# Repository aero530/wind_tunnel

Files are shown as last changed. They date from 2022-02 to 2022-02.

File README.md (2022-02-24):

# wind_tunnel

Low speed wind tunnel made from scrap material and 12V DC computer fans capable of 0 to 1200 ft/min.

Calibration process is documented [here](pitot%20static%20tube%20calibration%20process/Thermal%20Load%20Card%20Pitot%20Static%20Tube%20Calibration.pdf)

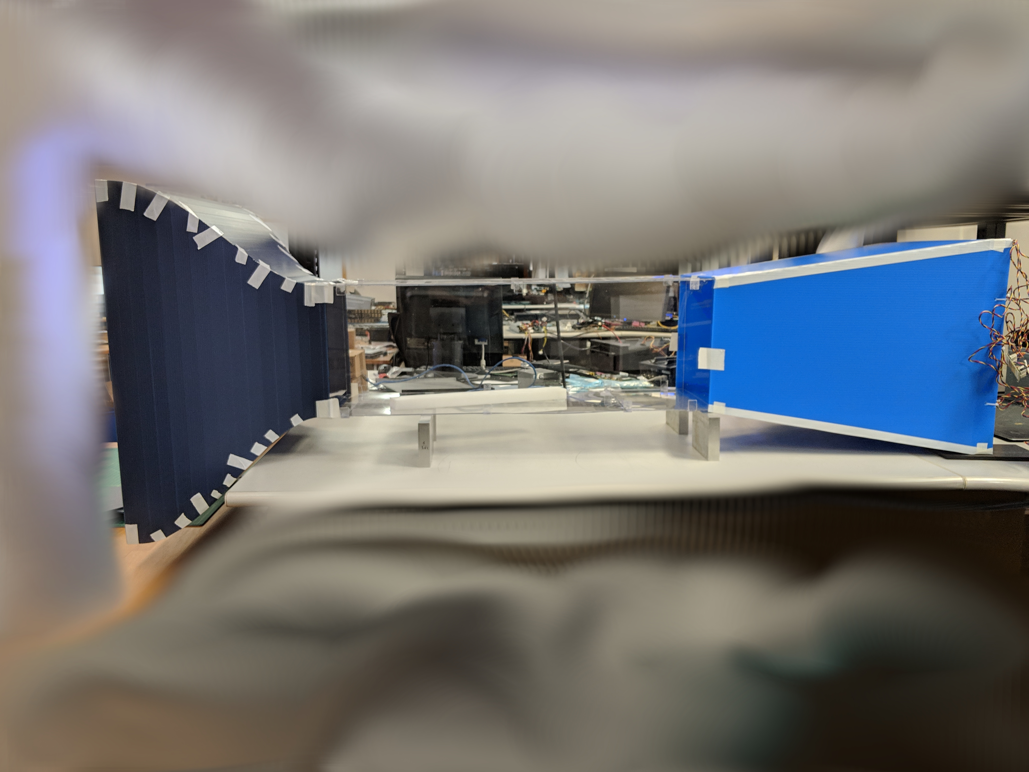
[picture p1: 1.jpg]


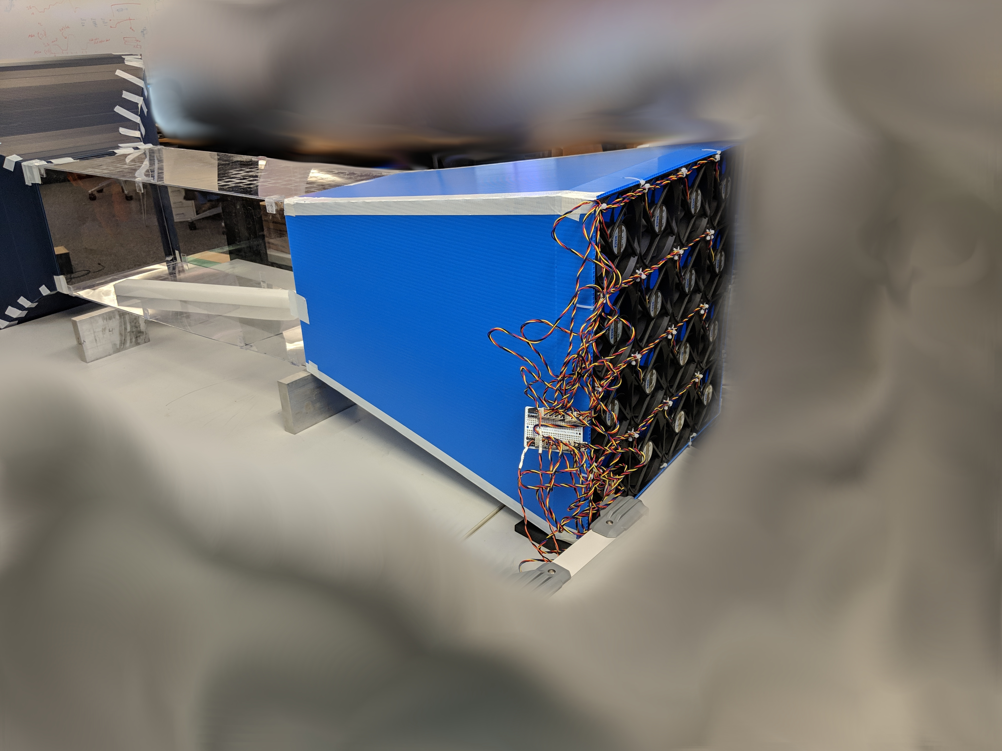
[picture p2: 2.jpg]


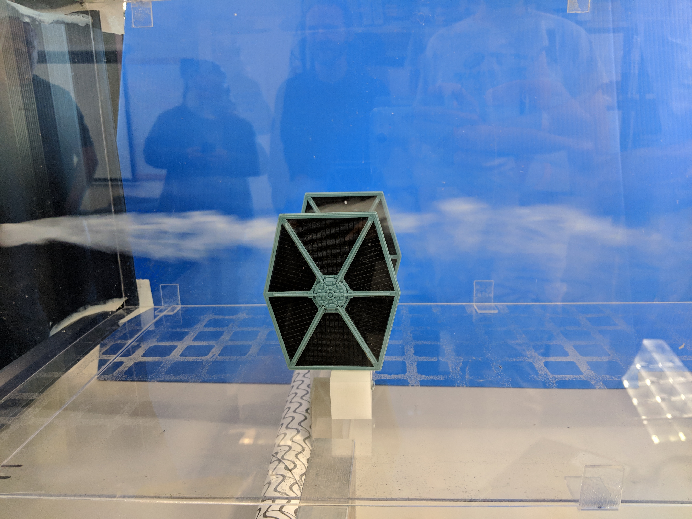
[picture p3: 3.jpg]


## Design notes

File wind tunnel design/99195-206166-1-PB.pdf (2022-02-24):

Indian Journal of Science and Technology, Vol 9(30), DOI: 10.17485/ijst/2016/v9i30/99195, August 2016

ISSN (Print) : 0974-6846
ISSN (Online) : 0974-5645

* Author for correspondence

## 1. Introduction

The wind tunnel is a tool to study fluid flows around a body and the forces generated by the fluid-structure interaction. Using such tool, it is possible to measure global and local flow velocities, as well as pressure and temperature around the body. A wind tunnel experiment provides the force and pressure values on the model and the flow visualization. It is a critical instrument in the quick and thorough design process of anything that involves fluid dynamics. Based on the flow through the tunnel circuit, the wind tunnel is of two types, open type and closed type. In open type, ambient air enters from one side and exits to the atmosphere after flowing through the tunnel. In closed type wind tunnel, a constant volume of air is allowed to pass through the tunnel circuit continuously Figure 1.

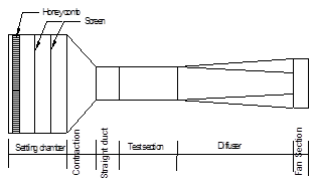
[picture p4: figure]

Figure 1. Schematic diagram showing different parts of wind tunnel.

Abstract

Objectives: This paper elucidate the entire procedure to design an open circuit subsonic wind tunnel which will be used to study the wind effect on the different prototypes of structural elements. Method: The existing guidelines and findings of the previous research works were followed for design calculation of different parts of the wind tunnel. Three design trials have been performed so as to achieve a velocity of 25 m/s at the test section. The final trial has been discussed in the body of the paper. Findings: The design includes a square test section of side 500 mm, to accommodate the model and required instrumentation in it, for force and pressure measurement. A straight section before the test chamber is provided to allow the output of contraction section to stabilize before it reaches the test section. Instead of using a curved wall shape a straight contraction profile with larger contraction length is used. The diffuser extends from the test section and its cross section changes from a square test section to an octagon of 311 mm side. The pressure drop and power required for the designed wind tunnel are calculated and tunnel performance curve is plotted. Application: The design being purely empirical, it requires computational validation before commencement of the construction of the wind tunnel. The investigators have actually made an attempt to design the same in the existing setup, which may be useful for different research purpose.
Keywords: Design of Open Circuit Wind Tunnel, Loss in Contraction Section, Power Requirement, Pressure Drop in

# Diffuser, Stilting Section, Tunnel Performance Curve

# Design of Low Cost Open Circuit Wind Tunnel – A Case Study

Mahesh K. Panda*

and Amiya K. Samanta
Department of Civil Engineering, National Institute of Technology Durgapur - 713209, West Bengal, India; mahesh26119@gmail.com, aksnitd@gmail.com

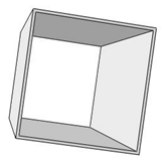
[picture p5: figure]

2 | Vol 9 (30) | August 2016 | www.indjst.org | Indian Journal of Science and Technology

Design of Low Cost Open Circuit Wind Tunnel – A Case Study

The main goal of wind tunnel design is to have uniform flow within the test chamber. Test chamber dimension depends on the type of test to be performed and the size of the model to be tested. The wind tunnel’s overall dimensions are key factors in its construction and running costs. The trade-off is required between the opposing needs to get a suitable design of the wind tunnel, satisfying the test requirements, space and budget constraints¹

. The design process starts by defining the test chamber dimensions and shape, after that the rest part of the wind tunnel is designed by keeping in view the dimensions of the test chamber.
Principal parts of an open type wind tunnel are the test section, contraction, diffuser, settling chamber and driving unit (Fan). This paper deals with the design of an open type wind tunnel to have minimum construction cost and the running cost.

## 2. Design Methodology

The open circuit wind tunnel is made of several distinct sections, the settling chamber, the contraction cone, the test section, the diffuser and the fan. Different parts are described as follows:

### 2.1 Test Section

The wind tunnel design starts with deciding the test section keeping an eye on the accessibility and installation of the test model and instrumentation. From the experimental investigations, it has been found that the blockage has an almost negligible effect on test results when it is about 10%²

. The test chamber length has to be in the range of 0.5-3 times its hydraulic diameter³,4. The test chamber is being designed to test the scaled model of a silo with length 250 mm and minimum L/D ratio 1. In order to have a blockage ratio less than 10% a square test chamber of 500 mm side is chosen Figure 2. The test will be carried out at a flow speed of 25 m/s. The pressure loss coefficient goes on increasing with increase in the test section Figure 3. So the length of test section should be as small as possible. The length of the test chamber was set to 1.25 m i.e. 2.215 times the hydraulic diameter of the test section.

Figure 2. Test section.

### 2.2 Contraction Cone

The contraction accelerates the flow to the test section, further reducing any variations in velocity. A contraction design satisfying all criteria will be such that the separation is just avoided and the exit non-uniformity is equal to or less than the maximum tolerable level for the desired application in shortest possible length⁵

. The contraction
starts with the selection of contraction ratio⁶

. For smaller
tunnels the contraction ratio should be in between 6 to 9. The length of the contraction should be in between 0.15 R to R. R being the hydraulic radius of the contraction section inlet. Too large contraction section avoids flow separation⁷
As shown in Figure 4, the pressure drop coefficient values go on decreasing with increase in CR, so the maximum allowable contraction ratio 9 is chosen. To avoid flow separation, a contraction of length of 900 mm is used, which is 20% longer than the maximum recommended value. For easier and cheaper construction a straight contraction shape is used instead of solving complex equations to get the wall shape. The nozzle exit cross section dimensions and shape are identical to the test chamber.
250 | 500 | 750 | 1000 | 1250 | 1500 | 1750

0.01

0.02

0.03

0.04

0.05

0.06

Pressure drop coefficent

Length of test section (mm)

Figure 3. Plot to show the pressure loss in a constant area section.

Mahesh K. Panda and Amiya K. Samanta

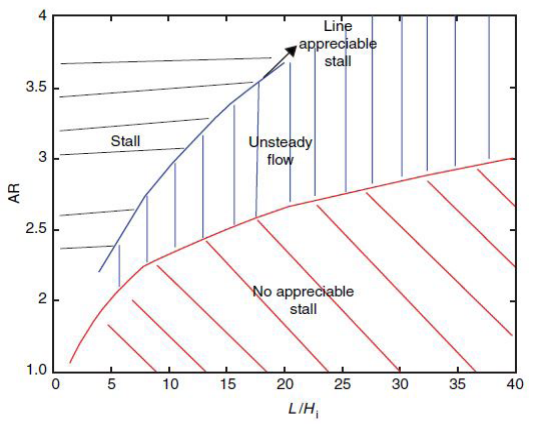
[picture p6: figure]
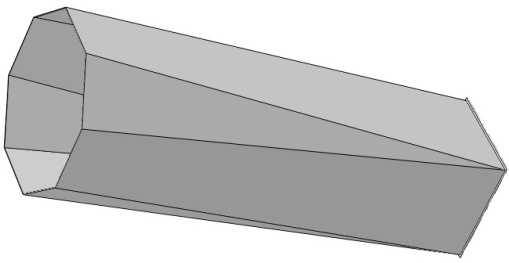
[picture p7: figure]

Vol 9 (30) | August 2016 | www.indjst.org | Indian Journal of Science and Technology | 3

5.5 6.0 6.5 7.0 7.5 8.0 8.5 9.0 9.5 10.0 10.5 11.0 0.0030

0.0032

0.0034

0.0036

0.0038

0.0040

0.0042

0.0044

0.0046

0.0048
Loss coefficient

Contraction Ratio

Loss coefficient

Figure 4. Contraction section pressure loss coefficient with contraction ratio.

### 2.3 Straight Section

Inserting a small settling duct before the test section can reduce the turbulence level to an acceptable level, for nonstreamlined shape of contraction wall⁸

. A straight section
of length 0.5 m has been inserted after the contraction, with an area of cross section equal to the testing chamber size. Figure 5 shows the straight section attached to the contraction cone.

Figure 5. A diagram showing the contraction cone with a straight section.

### 2.4 Diffuser

The diffuser is mainly used to reduce the velocity of flow in the shortest possible distance to reduce the load on drive system. The flow through the diffuser depends on its geometry defined by area ratio (ratio of outlet area to the inlet area) and diffuser angle (2θ), wall contour and diffuser cross-sectional shapes. The area ratio of the diffuser should be less than 2.5 and diffuser angle should be 5˚ – 7˚ for controlling flow separation. The minimum length of diffuser can be found from Equation,
. | (1)

Where, Dh1 is the inlet sections hydraulic diameter and is the half of the included angle of the diffuser cone.
| Assuming minimum diffusion angle (θe ) i.e. 5⁰ and
solving for L, the maximum of the minimum length of the diffuser is found to be 2.38 m, hence a diffuser of 2.5 m length is provided. An octagonal outlet is chosen with side 310 mm Figure 6. The diffuser area ratio is calculated as 1.86, which falls in the no stall region in Figure 7 with a diffusion angle 5.03⁰

Figure 6. A diagram showing the diffuser.

### 2.5 Settling Chamber

The aim of a settling chamber containing honeycombs and screens is to reduce the flow turbulence before it enters the cone. A selection of honeycomb and screens for a wind tunnel is very much dependent on the test type to which the tunnel is intended⁸

. The settling
chamber cross-sectional area matches the dimensions of contraction cone inlet i.e. 1.5 m x 1.5 m with a length equal to 1.25 m is used.

### 2.6 Honeycomb

The honeycomb removes the swirl from the incoming flow and minimizes the variation in both mean and fluctuating velocity⁹

. It should have sufficient flexural rigidity to withstand applied forces during operation without significant deformation. The primary design parameter for honeycomb is the ratio of length to cell hydraulic diameter (L/D) and porosity (flow area upon total area). Recommended L/D ratio for honeycomb is 6 to 8 with porosity nearly 0.8. A square shaped honeycomb, 3 mm

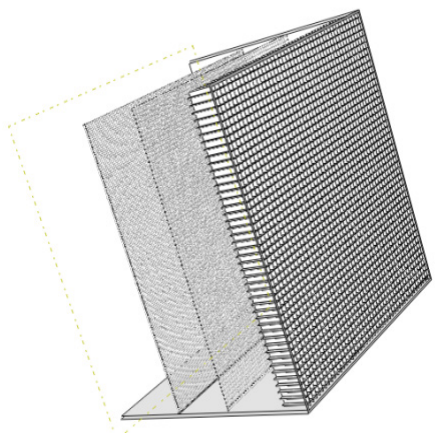
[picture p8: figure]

4 | Vol 9 (30) | August 2016 | www.indjst.org | Indian Journal of Science and Technology

thick and 27 mm size and 150 mm length is provided with a porosity value of 0.82. Figure 8 shows an arrangement of Honeycomb and screens in settling chamber.

Figure 8. Diagram showing the arrangement of honeycomb and screen.

### 2.7 Screens

Tensioned screens are placed in the settling chamber for the reduction of turbulence level of incoming flow, this breaks up the large scale turbulent eddies into a number of small scale eddies that subsequently decay. To be effective in reducing turbulence a screen must have porosity in the range 0.58–0.8⁹

. Screen porosity values over 0.8 are not suitable for good turbulence control while values below 0.58 lead to flow instability¹⁰. A clearance of 0.2 times the settling chamber diameter is required between the screens. Experimentally it is found that better turbulence control can be achieved when the finest screen is placed farthest downstream¹¹⁻¹³.
So a screen with 2 mm wire and porosity 0.69 is placed at a distance 340 mm from the start of the contraction i.e. 0.2 times the hydraulic diameter of the settling chamber and the 3 mm wire screen mesh with porosity 0.76 is placed at the same distance from the first screen.

### 2.8 Drive System

The drive system compensates the loss in the circuit and determines the movement of the fluid through the test section. For an air tunnel, two primary drive systems are a compressor and fan. In our case, an Axial fan will be used as these are high efficient and produce air flow with less turbulence. After the maximum required fan static pressure and volume flow rate have been estimated the maker’s performance chart can be consulted to choose a fan with optimum efficiency, RPM and required power¹⁴.

## 3. Losses in Wind Tunnel Circuit

For loss calculation, the tunnel can be divided into sections. The pressure loss in a tunnel section is defined as the mean loss of total pressure sustained by the stream, in passing through the particular section. The energy loss of each section can be written in dimensionless form as
pressure drop coefficient | | (2)

Where, is test section dynamic pressure given as
| | (3)

The losses in different parts of wind tunnel can be calculated as below:

### 3.1 Pressure Losses in Constant Area Sections

Considering a constant-area section (A), the pressure loss (p) along the duct is proportional to its length (L), hydraulic diameter (Dh

), fluid density (ρ) and constant of proportionality is the friction factor (f). The loss
coefficient is given by, | . | (4)
The friction loss coefficient can be determined by using universal law of friction to determine the friction factor in 4 to 6 iterations with an initial value of 1. In Equation is given as:
| | (5)

### 3.2 Pressure Loss in Diffuser

Pressure loss in the diffuser is due to the skin friction loss and the expansion loss. The main parameters are equivalent conical expansion angle ( ) and the ratio between inlet and outlet cross section areas (Ar

| | ). The
loss coefficient is the sum of the two loss factors, the first relates to friction and the second to expansion
| | (6)
For one dimensional flow, the frictional loss coefficient is
given as | | (7)

and the expansion loss is calculated by the empirical
relationship | | (8)
The term | can be expressed as a geometrical
function depending upon the expansion angle and the cross section shape of the diffuser. In our case > 5⁰

,
so = A3+B3 , | | (9)
for circular section the values of A3 and B3 are -0.0966

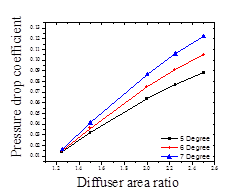
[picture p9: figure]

Vol 9 (30) | August 2016 | www.indjst.org | Indian Journal of Science and Technology | 5

and 0.04672 respectively. For square section the values of A3 and B3 are -0.0132 and 0.05866 respectively. Figure 9 shows the variation of pressure loss coefficient with area ratio for different diffusion angle.

Figure 9. Plot showing the pressure drop for various diffusion angle.

### 3.2 Contraction Section Loss

The pressure loss in contraction is due to skin friction. The loss coefficient in the contraction is given by¹⁵:

(10)
Where, L0

is the length of contraction, D0

the test
section diameter, Di

the inlet cone diameter, and f is friction coefficient.

### 3.2 Stilting Section Loss

The losses in the settling chamber are primarily due to the honeycomb and screens used for turbulence reduction. The loss in the honeycomb can be calculated from the formula
(11)

Where
(12)

The screen loss coefficient can be calculated

(13)

Is screen solidity and is the screen porosity. is the mesh factor equal to 1.0 for new metal wire , 1.3 for average circular metal wire, and 2.1 fir silk thread and kRn is given as

(14)
From the Equations it is clear that the pressure drop through the honeycomb and the screen depends only upon the characteristics of the same and becomes constant when the Reynolds number values exceed some critical value. Honeycomb loss depends on L/D ratio of honeycomb and porosity while the pressure drop through the screen is dependent on the type of wire and the porosity.

## 4. Power required in Wind Tunnel

Power required for maintaining a steady flow through the wind tunnel is equal to the total losses occurring in the flow through the tunnel. These losses are due to kinetic energy being dissipated by vortices and turbulence. The loss in kinetic energy, which appears as a decrease in total pressure must be compensated by a pressure rise, usually provided by a fan. Thus if the power input to the fan is P (i.e. the motor shaft output) and the fan has an efficiency the equation balancing the energy input to the stream to the energy losses in the tunnel is
(15)
The required power for a given section size and flow conditions depends on the sum of the pressure drop coefficient (ki

) in the individual tunnel sections. The pressure loss equation for subsonic flow in wind tunnel is
given as | | (16)
In the designed tunnel the various loss coefficient are given in Table 1, for a speed of 25m/s at the test section. Speed at fan section: = (25*0.5*0.5)/ (0.25*3.142*.75*.75)
| = 14.144 m/s
The pressure loss in the tunnel circuit is equal to:
= ( | ) ∑ ki + loss at fan section | (17)
= 0.5*1.225*25² *1.3553+ 0.5*1.225*14.144*14.144 =641.36 Pa

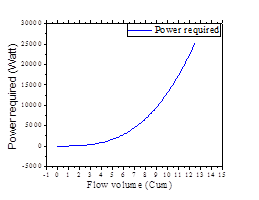
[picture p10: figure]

6 | Vol 9 (30) | August 2016 | www.indjst.org | Indian Journal of Science and Technology

Table 1. Tunnel pressure loss coefficient at test section velocity 25 m/s
Wind Tunnel Section | Loss coefficient
Honeycomb | 0.2200
Screen 1 | 0.4117
Screen 2 | 0.6049
Contraction | 0.0037
Straight section | 0.149
Test Section | 0.372
Diffuser | 0.0629
Total | 1.3553

The power required by the tunnel is equal to:
= Q * ∆Pa = (A*V)* ∆Pa | (18)
= (0.25*3.142*0.75²

*14.144)*641.36 = 4008.5 Watt

The power required for given flow in the wind tunnel test section is calculated and the same is plotted as the tunnel performance curve. Figure 10 shows the tunnel performance curve for the designed wind tunnel. Fan performance curves, which are supplied by the fan manufactures, can be plotted on the tunnel performance curve and the fan with maximum efficiency that intersects the tunnel performance curve is to be chosen for use in the tunnel.

Figure 10. Tunnel performance.

## 5. Conclusion

The fan/motor to be fitted in the tunnel should be chosen conservatively to have desired flow velocity in the wind tunnel test section to cater the unseen losses in the tunnel. Further due to the purely empirical design of wind tunnel, as per the guidelines of the previous researchers, the design is required to be verified computationally as well as experimentally. First the tunnel design is to be tested for the desired flow quality and pressure loss in the tunnel computationally through any high-end simulation software (ABAQUS or ANSYS) if satisfactory results are found then the wind tunnel can be built. Before carrying out any experiment, the wind tunnel performance is to be tested and calibrated.
To ensure good performance of the structures subjected to wind loads, their behavior must be anticipated in advance by the design engineer¹⁶. Model studies through wind tunnel facilitate the same for the intended structure. So it is a useful tool in wind engineering.

## 6. References

1. Cattafesta L, Bahr CJ, Mathew J. Fundamentals of wind‐ tunnel design. Encyclopedia of Aerospace Engineering; 2010 Dec. p. 1–10.
2. Roy S, Saha UK. An adopted blockage factor correlation approach in wind tunnel experiments of a Savonius-style wind turbine. Energy Conversion and Management. 2014; 86(6):418–27.
3. Arifuzzaman, MM. Design construction and performance test of a low cost subsonic wind tunnel. IOSR Journal of Engineering. 2012 Oct; 2(10):83–92.
4. Barlow JB, Rae WH, Pope A. Low-speed wind tunnel testing. 3rd Ed. Wind Tunnel Design. United States of America: John Willey and Sons Publ; 1999.
5. Abdalhamed AS, Yassen YEl-S, Elssaka MM. Design optimization of three dimensional geometry of wind tunnel contraction. Ain Shams Engineering Journal. 2015 Mar; 6(1):281–8.
6. Fang FM, Chen JC, Hong YT. Experimental and analytical evaluation of flow in a square to square wind tunnel contraction. Journal of Wind Engineering and Industrial Aerodynamics. 2011 Mar; 89(3-4):247–62.
7. Mehta RD, Bradshaw P. Design rules for small low speed wind tunnels. The Aeronautical Journal. 1979 Nov; 83(827):443–9.
8. Building a wind tunnel: It will blow your mind. 2008. Available from: http://www.tomcarlone.com/Wind TunnelProject/WindTunnelReport.pdf
9. Gharbanian K, Soltani MR, Manshadi D. Experimental investigation on turbulence reduction in subsonic wind tunnels. Aerospace Science and Technology. 2011 Mar; 15(2):137–47.

Vol 9 (30) | August 2016 | www.indjst.org | Indian Journal of Science and Technology | 7
10. Mehta RD. Turbulent boundary layer perturbed by a screen. AIAA Journal. 1985 Sep; 23(9):1335–42.
11. Quiterio PR, Velazquez MT, Eslava GT, Eslava RT, Florencio SS, Francis JA. Wind tunnel at LABINTHAP (Updated). Energy and Power Engineering. 2011 Sep; 3(4):565–73.
12. Groth J, Johansson AV. Turbulence reduction by screen. Journal of Fluid Mechanics. 1988 May; 197:139–55.
13. Gharbanian K, Soltani MR, Manshadi MD. Experimental investigation on turbulence reduction in subsonic wind tunnels. Aerospace Science and Technology. 2011 Mar; 15(2):137–47.
14. Bleier FP. Fan handbook: Selection application and design. New York: McGraw Hills Publications; 1998.
15. D Space. 2016. Available from: https://en.wikipedia.org/wiki/DSpace
16. Kumar BD, Swami BLP. Wind effects on tall building frames-influence of dynamic parameters. Indian Journal of Science and Technology. 2010 May; 3(5):583–7.

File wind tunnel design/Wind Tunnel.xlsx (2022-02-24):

Test item cross section area | 8 | in^2
Test height | 12 | in | assume square test section
Test area ratio | 18 |  | should be >10
Test Hydraulic Diameter | 12 | in
Test Length Ratio | 2 |  | should be 0.5 to 3 times Dh
Test Length | 24 | in
Contraction Ratio | 5.84 |  | should be 4 to 9
Contraction Angle | 31.26 | deg
Inlet height | 29.00 | in
Contraction Length | 14.00 | in
Contraction Length Ratio | 0.483 |  | should be 0.15 to 1
Desired LFM | 1500 | ft/min
CFM | 1500 | CFM
Diffuser Angle | 7.94 | deg | should be 5-8deg
Diffuser Area Ratio | 2.5 |  | should be less than 2.5
Exit height | 18.974 | in
Exit height | 481.931 | mm
Diffuser Length | 25.000 | in
Per Fan Airflow | 100 | CFM
# Fans that fit | 16
# Fans needed | 15
Total Length | 63.002 | in
Total Length | 5.25 | ft

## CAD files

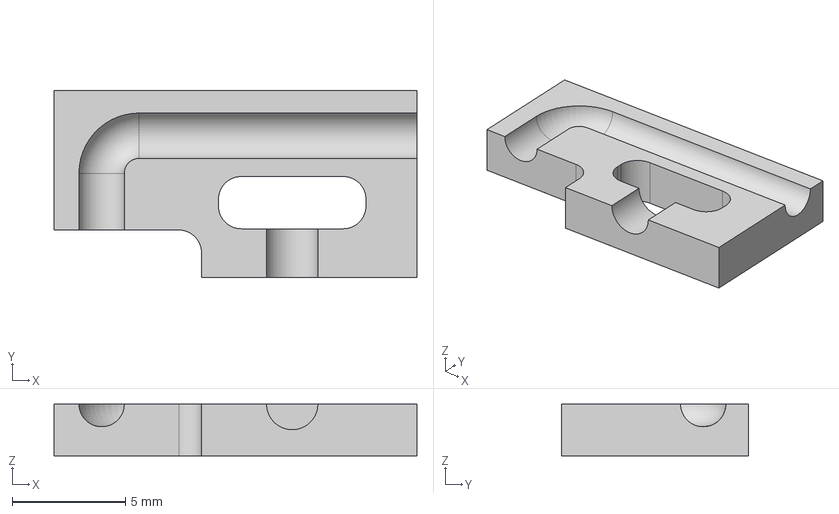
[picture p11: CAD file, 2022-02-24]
pitot static tube design/cad/SDP3X pitot tube 1 v1.step
16.0 x 8.26 x 2.29 mm

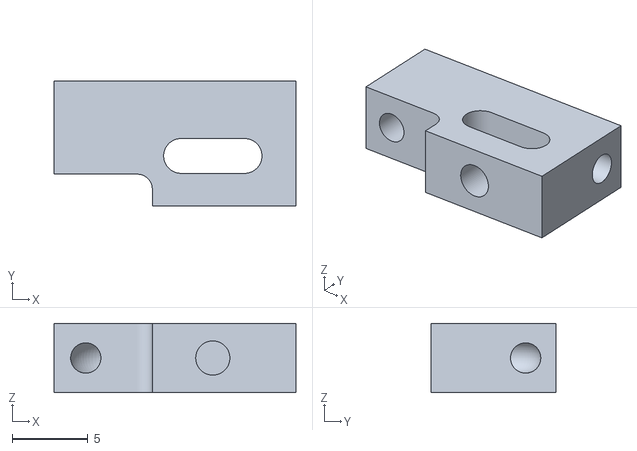
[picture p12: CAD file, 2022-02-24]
pitot static tube design/SDP3X pitot tube solid.STL
16.0 x 8.26 x 4.57

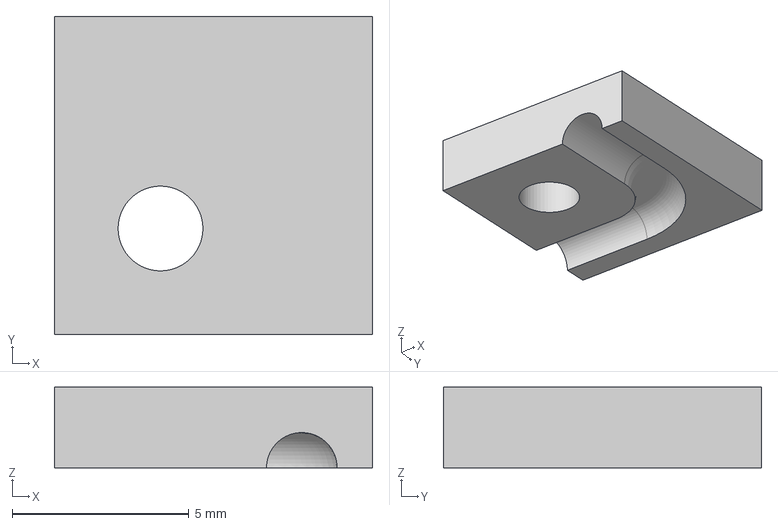
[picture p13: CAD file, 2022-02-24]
pitot static tube design/cad/Amphenol DLHR-L01D-E1BD Pitot Tube B v1.step
9.00 x 9.00 x 2.29 mm

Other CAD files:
pitot static tube design/cad/SDP3X pitot tube 2 v1.step
pitot static tube design/cad/Amphenol DLHR-L01D-E1BD Pitot Tube A v1.step
pitot static tube design/cad/Amphenol DLHR-L01D-E1BD Pitot Tube A v1.iges
pitot static tube design/cad/Amphenol DLHR-L01D-E1BD Pitot Tube A v1.stl
pitot static tube design/cad/Amphenol DLHR-L01D-E1BD Pitot Tube B v1.iges
pitot static tube design/cad/Amphenol DLHR-L01D-E1BD Pitot Tube B v1.stl
pitot static tube design/cad/SDP3X pitot tube 1 v1.iges
pitot static tube design/cad/SDP3X pitot tube 1 v1.stl
pitot static tube design/cad/SDP3X pitot tube 2 v1.iges
pitot static tube design/cad/SDP3X pitot tube 2 v1.stl

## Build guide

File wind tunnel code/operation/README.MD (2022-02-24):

# Wind Tunnel

This code runs a profile on the wind tunnel and collects data from the thermal load card and the hot wire anemometer.  It is super hacky and disgusting code that controls the actual wind tunnel using a python script and collects data from the hot wire anemometer and thermal load card using javascript.

## To run, please:
1. Install python3
2. Install python modules
	`pip install pyserial`
3. Install node/npm
4. Install the required packages by navigating to the containing directory and running `npm install`
5. Configure the settings for COM and test parameters in runTest.py and windTunnel.js
6. From the containing directory, execute `node windTunnel`

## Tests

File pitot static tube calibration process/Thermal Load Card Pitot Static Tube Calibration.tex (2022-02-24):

\documentclass[]{article}
\usepackage{array}
\usepackage{graphicx} % Required for including pictures
\usepackage{float} % float package used so figure location can be forced

\usepackage[top=1in,bottom=1in,left=1in,right=1in,headsep=10pt,letterpaper]{geometry} % Page margins

%----------------------------------------------------------------------------------------
%	FONTS
%----------------------------------------------------------------------------------------

\usepackage{avant} % Use the Avantgarde font for headings
%\usepackage{times} % Use the Times font for headings
\usepackage{mathptmx} % Use the Adobe Times Roman as the default text font together with math symbols from the Sym­bol, Chancery and Com­puter Modern fonts

\usepackage{microtype} % Slightly tweak font spacing for aesthetics
\usepackage[utf8]{inputenc} % Required for including letters with accents
\usepackage[T1]{fontenc} % Use 8-bit encoding that has 256 glyphs

\newenvironment{conditions}
{\par\vspace{\abovedisplayskip}\noindent\begin{tabular}{>{$}l<{$} @{${}={}$} l}}
	{\end{tabular}\par\vspace{\belowdisplayskip}}

%opening
\title{Thermal Load Card Pitot Static Tube Calibration}
\author{Phil Spindler}

\begin{document}

\maketitle

\begin{abstract}

The following summarizes the process for calibrating the thermal load card pitot static tube velocity measurements.  During this process a wind tunnel was used to provide a uniform stream of air with controllable velocity and a hot wire anemometer was used to provide the reference velocity measurements.  The resulting calibration allows for the pitot static tube to produce results within $5\%$ of the hot wire anemometer readings for velocities above $30 \frac{ft}{min}$.

\end{abstract}

\section{Physics Based Calculation}

The primary calculation to convert the differential pressure measured across the ports of the pitot static tube is shown in Equation \ref{basePhysics}.

\begin{equation}\label{basePhysics}
V = \frac{P_0}{P}\sqrt{\frac{T}{T_0}}\sqrt{2 \frac{\partial P_{sensor}}{\rho_0}}
\end{equation}
where:
\begin{conditions}
 V		& velocity in $\frac{m}{s}$ \\
 P_0	& sensor reference pressure $\left[ 966 \mbox{ mbar} \right] $ \\
 P		& atmospheric pressure $\left[1013.25 \mbox{ mbar} \right] $ \\
 T_0	& sensor reference temperature $\left[298.15 \mbox{ K} \right] $ \\
 T		& sensor measured temperature in K \\
 \partial P_{sensor}	& sensor zero calibrated differential pressure in Pa \\
 \rho_0	& density of air $ \left[ 1.1289 \frac{kg}{m^3} \right] $ \\
\end{conditions}

\noindent
Simplifying Equation \ref{basePhysics} gives

\begin{equation}\label{simplifiedPhysics}
V = 0.073490358 \sqrt{ T * \partial P_{sensor} }
\end{equation}

\noindent
Equation \ref{simplifiedPhysics} can be converted from $\frac{m}{s}$ to $\frac{ft}{min}$ by multiplying by $196.85$ leading to Equation \ref{simplifiedPhysicsFt}.

\begin{equation}\label{simplifiedPhysicsFt}
V = 14.4665769723 \sqrt{ T * \partial P_{sensor} }
\end{equation}

\noindent
Equation \ref{simplifiedPhysicsFt} provides the basis to convert the temperature and differential pressure readings from the pitot static tube sensor to velocity.  The calculated velocity values were then put through a calibration process to better match readings from the hot wire anemometer.

\section{Calibration}

The calibration was performed by taking measurements from the pitot static tube on the card and a hot wire anemometer next to the card (approximately 1in away).  The thermal load card was setup in a wind tunnel and the wind tunnel speed was varied through it's entire range (0-100\%) in 1\% increments.  The wind tunnel was held at a constant speed for 30 seconds between each step as shown in Figure \ref{fig:tunnelSetting}.

\begin{figure}[H]
	\centering
	\caption{Wind Tunnel Setting}
	\label{fig:tunnelSetting}
\end{figure}

\noindent
The velocity in the wind tunnel as recored by the hot wire anemometer and results from the pitot static tube based on Equation \ref{simplifiedPhysicsFt} are shown in Figure \ref{fig:rawVelocity}.  The results shown here (and used in subsequent analysis) are an average of 10 seconds of data centered on the middle of the wind tunnel speed steps shown in Figure \ref{fig:tunnelSetting}.  The 10 second subset of data was selected to avoid velocity instabilities in the wind tunnel immediately after wind tunnel setting changes.

\begin{figure}[H]
	\centering
	\caption{Uncalibrated Velocity}
	\label{fig:rawVelocity}
\end{figure}

\noindent
Figure \ref{fig:calibration} shows the physics based calculation of velocity relative to readings from the hot wire anemometer.  This relation was used to create a two part curve fit to calibrate the pitot static tube results with the hot wire anemometer results.  The correlation is linear for velocities above $362.645 \frac{ft}{min}$.  Below that point, the pitot static tube response is non-linear and fit with a second order polynomial.  

\begin{figure}[H]
	\centering
	\caption{Pitot Tube Calibration Curves}
	\label{fig:calibration}
\end{figure}

\noindent
Figure \ref{fig:result} shows the calibrated velocity results.  In this image, the $1:1$ Line shows an ideal fit between the two parameters.  When the airflow velocity is less than approximately $30 \frac{ft}{min}$ the pitot static tube provides unreliable results (with errors up to $93\%$).  Beyond this lower threshold the average error is $1.02\%$ and the maximum error is $4.59\%$.

\begin{figure}[H]
	\centering
	\caption{Calibration Result}
	\label{fig:result}
\end{figure}

\end{document}

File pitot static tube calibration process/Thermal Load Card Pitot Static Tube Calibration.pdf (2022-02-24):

# Thermal Load Card Pitot Static Tube Calibration

Phil Spindler

May 1, 2019

Abstract

The following summarizes the process for calibrating the thermal load card pitot static tube velocity measurements. During this process a wind tunnel was used to provide a uniform stream of air with controllable velocity and a hot wire anemometer was used to provide the reference velocity measurements. The resulting calibration allows for the pitot static tube to produce results within 5% of the hot wire anemometer readings for velocities above 30 ft
min .

## 1 Physics Based Calculation

The primary calculation to convert the differential pressure measured across the ports of the pitot static tube is shown in Equation 1.

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
∂Psensor

ρ0

(1)

where:

V = velocity in m
s
P0 | = sensor reference pressure [966 mbar]
P | = atmospheric pressure [1013.25 mbar]
T0 | = sensor reference temperature [298.15 K]
T | = sensor measured temperature in K
∂Psensor = sensor zero calibrated differential pressure in Pa ρ0 = density of air h
1.1289 kg
m³

i

Simplifying Equation 1 gives

V = 0.073490358p
T ∗ ∂Psensor | (2)

Equation 2 can be converted from m
s

to ft
min by multiplying by 196.85 leading to Equation 3.

V = 14.4665769723p
T ∗ ∂Psensor | (3)

Equation 3 provides the basis to convert the temperature and differential pressure readings from the pitot static tube sensor to velocity. The calculated velocity values were then put through a calibration process to better match readings from the hot wire anemometer.

## 2 Calibration

The calibration was performed by taking measurements from the pitot static tube on the card and a hot wire anemometer next to the card (approximately 1in away). The thermal load card was setup in a wind tunnel and the wind tunnel speed was varied through it’s entire range (0-100%) in 1% increments. The wind tunnel was held at a constant speed for 30 seconds between each step as shown in Figure 1.

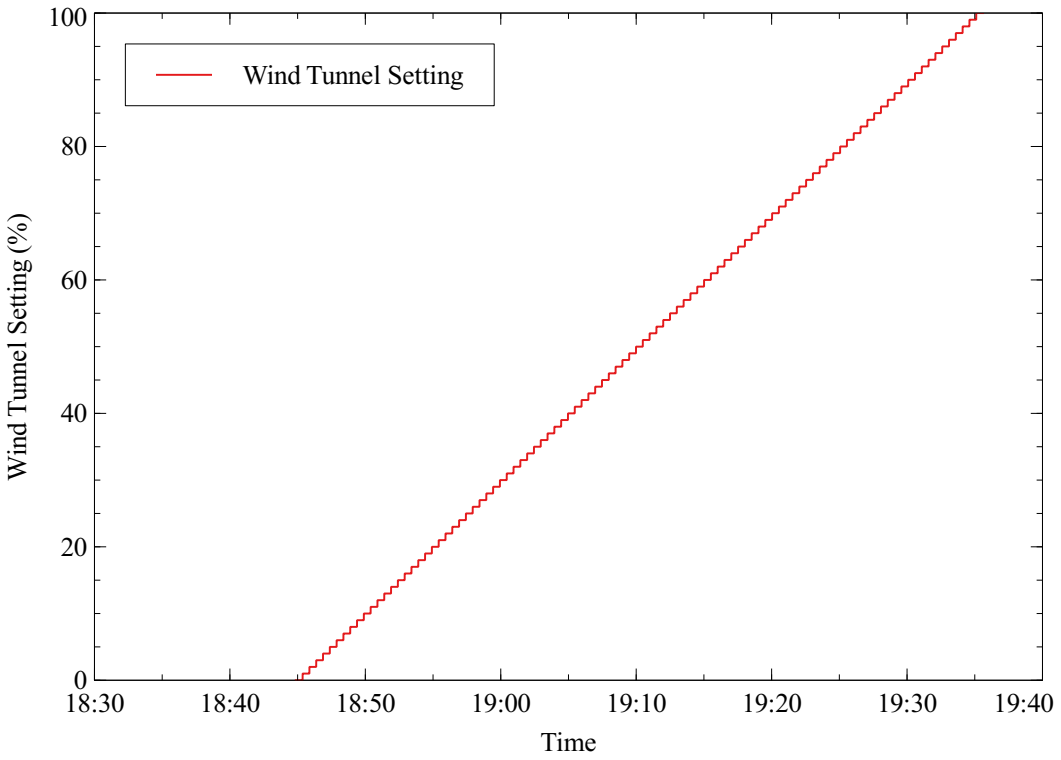
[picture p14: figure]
Wind Tunnel Setting; Win; unn; ettin; Time

Figure 1: Wind Tunnel Setting

The velocity in the wind tunnel as recored by the hot wire anemometer and results from the pitot static tube based on Equation 3 are shown in Figure 2. The results shown here (and used in subsequent analysis) are an average of 10 seconds of data centered on the middle of the wind tunnel speed steps shown in Figure 1. The 10 second subset of data was selected to avoid velocity instabilities in the wind tunnel immediately after wind tunnel setting changes.

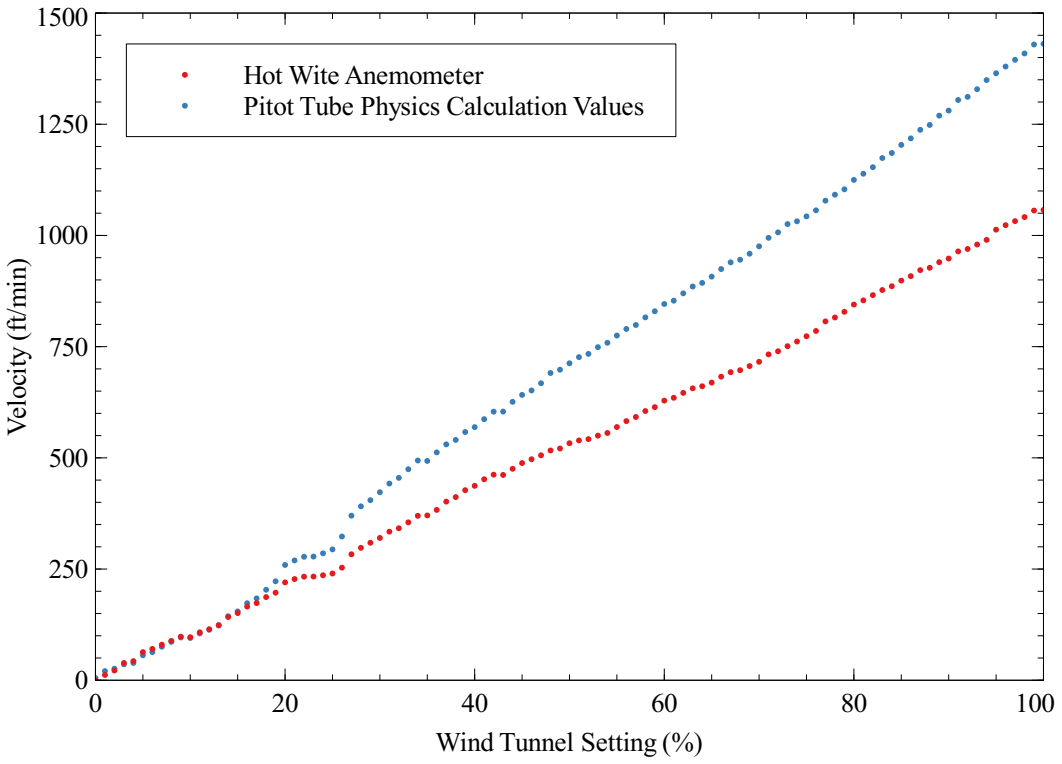
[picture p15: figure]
Hot Wite Anemometer Pitot Tube Physics Calculation Values; Velo; city (ft/min); Wind Tunnel Setting (%)

Figure 2: Uncalibrated Velocity

Figure 3 shows the physics based calculation of velocity relative to readings from the hot wire anemometer. This relation was used to create a two part curve fit to calibrate the pitot static tube results with the hot wire anemometer results. The correlation is linear for velocities above 362.645 ft
min . Below that point, the pitot static tube response is non-linear and fit with a second order polynomial.

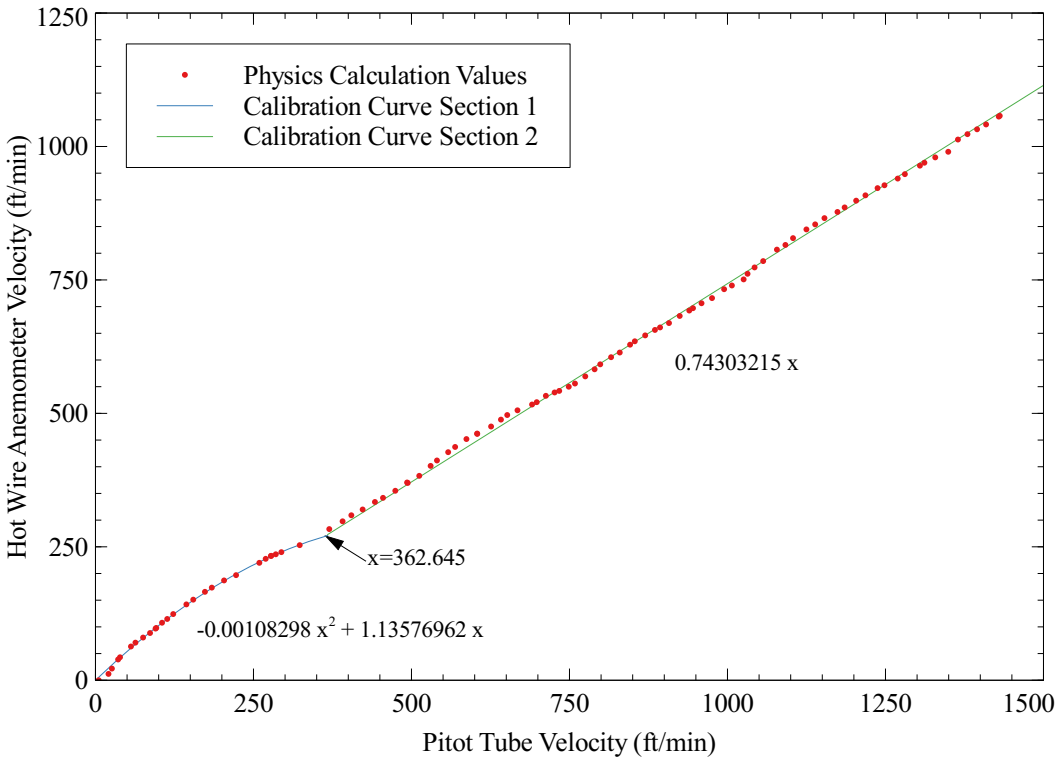
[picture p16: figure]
Physics Calculation Values Calibration Curve Section 1 Calibration Curve Section 2; ot Wir; ete; Velo; city (ft/min); Pitot Tube Velocity (ft/min)

Figure 3: Pitot Tube Calibration Curves

Figure 4 shows the calibrated velocity results. In this image, the 1 : 1 Line shows an ideal fit between the two parameters. When the airflow velocity is less than approximately 30 ft
min the pitot static tube provides unreliable results (with errors up to 93%). Beyond this lower threshold the average error is 1.02% and the maximum error is 4.59%.

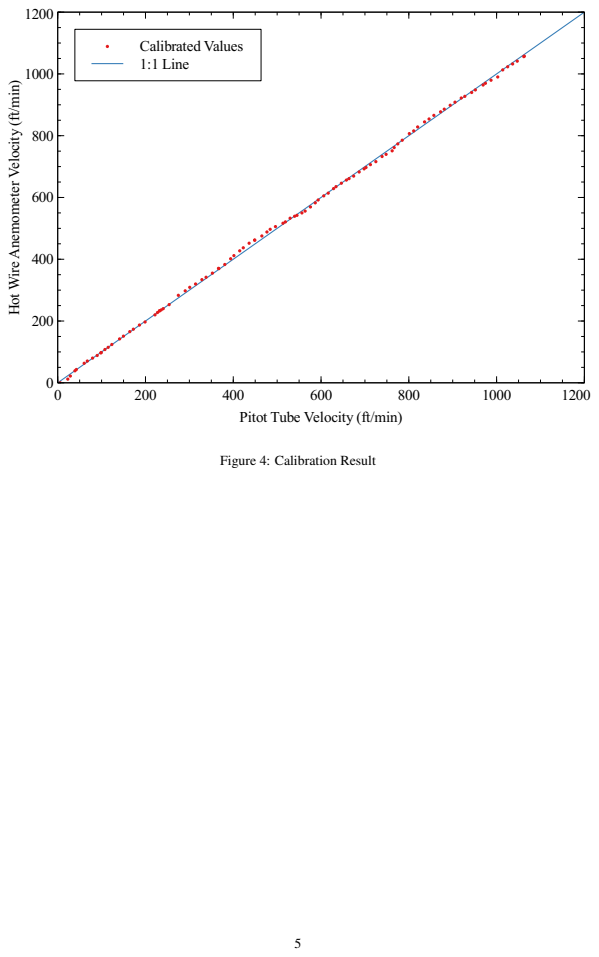
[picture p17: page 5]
Calibrated Values 1:1 Line; ot Wir; ete; Velo

city (ft/min)

Pitot Tube Velocity (ft/min)

Figure 4: Calibration Result

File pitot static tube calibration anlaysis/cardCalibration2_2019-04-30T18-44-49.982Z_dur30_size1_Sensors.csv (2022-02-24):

timestamp | pitotPressureZero | pitotPressureRaw | pitotTemperature | pitotVelocity | hotWireTemperature | hotWireVelocity
1556649890.056 | 0.00294499 | 0.02500000 | 24.395000 | 34.55925400 | 0 | 0
1556649890.151 | 0.00294499 | 0.02500000 | 24.360001 | 34.55868900 | 0 | 0
1556649890.263 | 0.00294499 | 0.02500000 | 24.395000 | 34.55925400 | 0 | 0
1556649890.359 | -0.00122167 | 0.02083333 | 24.379999 | 0.00000000 | 0 | 0
1556649890.455 | 0.00294499 | 0.02500000 | 24.375000 | 34.55892900 | 24 | 0
1556649890.551 | -0.00122167 | 0.02083333 | 24.415001 | 0.00000000 | 24 | 0
1556649890.663 | -0.00122167 | 0.02083333 | 24.365000 | 0.00000000 | 24 | 0
1556649890.759 | -0.00122167 | 0.02083333 | 24.410000 | 0.00000000 | 24 | 0
1556649890.855 | 0.00294499 | 0.02500000 | 24.355000 | 34.55860900 | 24 | 0
1556649890.967 | 0.00294499 | 0.02500000 | 24.400000 | 34.55933400 | 23.9 | 0
1556649891.063 | -0.00122167 | 0.02083333 | 24.395000 | 0.00000000 | 23.9 | 0
1556649891.159 | 0.00294499 | 0.02500000 | 24.375000 | 34.55892900 | 23.9 | 0
1556649891.255 | -0.00122167 | 0.02083333 | 24.370001 | 0.00000000 | 23.9 | 0
1556649891.367 | -0.00122167 | 0.02083333 | 24.375000 | 0.00000000 | 23.9 | 0
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

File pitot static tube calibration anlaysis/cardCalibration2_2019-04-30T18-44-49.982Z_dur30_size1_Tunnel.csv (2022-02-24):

timestamp | percentSetting | PWM1 | PWM2
1556649892.0691314 | 0 | 0 | 0
1556649892.1191533 | 0 | 0 | 0
1556649892.1698017 | 0 | 0 | 0
1556649892.220153 | 0 | 0 | 0
1556649892.2707539 | 0 | 0 | 0
1556649892.3209362 | 0 | 0 | 0
1556649892.3711548 | 0 | 0 | 0
1556649892.4213438 | 0 | 0 | 0
1556649892.471422 | 0 | 0 | 0
1556649892.5215974 | 0 | 0 | 0
1556649892.5717719 | 0 | 0 | 0
1556649892.6219404 | 0 | 0 | 0
1556649892.672119 | 0 | 0 | 0
1556649892.7224834 | 0 | 0 | 0
1556649892.7731366 | 0 | 0 | 0
1556649892.823411 | 0 | 0 | 0
1556649892.8736649 | 0 | 0 | 0
1556649892.9238477 | 0 | 0 | 0
1556649892.974082 | 0 | 0 | 0
1556649893.0242414 | 0 | 0 | 0
1556649893.0747085 | 0 | 0 | 0
1556649893.1248355 | 0 | 0 | 0
1556649893.1749 | 0 | 0 | 0
1556649893.2250714 | 0 | 0 | 0
1556649893.2752366 | 0 | 0 | 0
1556649893.3254352 | 0 | 0 | 0
1556649893.3764274 | 0 | 0 | 0
1556649893.4265983 | 0 | 0 | 0
1556649893.4767723 | 0 | 0 | 0
1556649893.5269136 | 0 | 0 | 0
1556649893.57775 | 0 | 0 | 0
1556649893.6279302 | 0 | 0 | 0
1556649893.678247 | 0 | 0 | 0
1556649893.7284248 | 0 | 0 | 0
1556649893.778579 | 0 | 0 | 0
1556649893.8296824 | 0 | 0 | 0
1556649893.8797042 | 0 | 0 | 0
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

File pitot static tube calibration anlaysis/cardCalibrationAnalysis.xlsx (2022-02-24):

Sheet: 2sec data window
 | avgHotWireTemperature | avgHotWireVelocity | avgPitotCalculatedVelocity | avgPitotCalculatedVelocityRaw | avgPitotPressureRaw | avgPitotPressureZero | avgPitotTemperature | avgPitotVelocity | calibrationSensorIndexEnd | calibrationSensorIndexStart | calibrationTimeEnd | calibrationTimeStart | middleTime | startingIndex | startingTime | Calibrated Pitot Velocity | Error in Calibrated Velocity
0 | 23.93684211 | 0 | 9.369786541 | 38.22471609 | 0.02346491105 | 0.001409904737 | 24.38499979 | 21.82680347 | 180 | 161 | 1556649908 | 1556649906 | 1556649907 | 0 | 1556649892 | 10.49498826 | #DIV/0!
1 | 23.91 | 13 | 20.73251447 | 42.46289259 | 0.0289583365 | 0.0069033265 | 24.36849995 | 39.5500133 | 480 | 460 | 1556649938 | 1556649936 | 1556649937 | 597 | 1556649922 | 22.97235049 | 76.71%
2 | 23.8 | 21.42105263 | 26.23891775 | 45.40393157 | 0.03311404105 | 0.01105903158 | 24.32000021 | 43.52567021 | 779 | 760 | 1556649968 | 1556649966 | 1556649967 | 1193 | 1556649952 | 28.92037405 | 35.01%
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

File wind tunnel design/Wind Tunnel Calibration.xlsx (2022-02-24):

Tunnel base convertion from %setting to the PWM percentages for each fan bank is a linear relationship defined by:
 | pwm min | pwm scale
pwm1 | 10 | 0.9000
pwm2 | 20 | 1.2500
Tunnel was ran with the base pwm values and airflow was measured with a hot wire anemometer. This data is marked as round 1.
The goal is to have a linear relationship between wind tunnel % setting and airflow velocity. The raw pwm settings produced a two section curved response (see graph).
percent | pwm1 | pwm2 | hot wire round 1 | desired vel (vel = 10.68 * percent setting)
100 | 100 | 100 | 1068 | 1068
95 | 95.5 | 93.75 | 1047 | 1014.6
90 | 91 | 87.5 | 1011 | 961.2
85 | 86.5 | 81.25 | 960 | 907.8
80 | 82 | 75 | 921 | 854.4
75 | 77.5 | 68.75 | 868 | 801
70 | 73 | 62.5 | 814 | 747.6
65 | 68.5 | 56.25 | 744 | 694.2
60 | 64 | 50 | 694 | 640.8
55 | 59.5 | 43.75 | 627 | 587.4
50 | 55 | 37.5 | 559 | 534
45 | 50.5 | 31.25 | 501 | 480.6
40 | 46 | 25 | 433 | 427.2
35 | 41.5 | 18.75 | 340 | 373.8
30 | 37 | 12.5 | 255 | 320.4
25 | 32.5 | 6.25 | 216 | 267
20 | 28 | 0 | 196 | 213.6
15 | 23.5 | -6.25 | 165 | 160.2
10 | 19 | -12.5 | 129 | 106.8
5 | 14.5 | -18.75 | 78 | 53.4
0 | 10 | -25 | 0 | 0
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

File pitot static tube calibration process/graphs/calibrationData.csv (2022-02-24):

Wind Tunnel Setting (%) | avgHotWireTemperature | avgHotWireVelocity | avgPitotCalculatedVelocity | avgPitotCalculatedVelocityRaw | avgPitotPressureRaw | avgPitotPressureZero | avgPitotTemperature | avgPitotVelocity | calibrationSensorIndexEnd | calibrationSensorIndexStart | calibrationTimeEnd | calibrationTimeStart | middleTime | startingIndex | startingTime | Calibrated Pitot Velocity | Error in Calibrated Velocity
0 | 23.92525253 | 0 | 5.112413343 | 37.40954168 | 0.022474745 | 0.000419742 | 24.38525251 | 13.61417474 | 220 | 121 | 1556649912 | 1556649902 | 1556649907 | 0 | 1556649892 | 5.77821816 | nan
1 | 23.93 | 11.88 | 20.60716638 | 42.40209645 | 0.028875003 | 0.006819993 | 24.37335005 | 39.44352272 | 520 | 420 | 1556649942 | 1556649932 | 1556649937 | 597 | 1556649922 | 22.94510032 | 93.14%
2 | 23.81010101 | 21.88888889 | 25.99870872 | 45.26556761 | 0.032912464 | 0.010857454 | 24.32055565 | 43.33274154 | 819 | 720 | 1556649972 | 1556649962 | 1556649967 | 1193 | 1556649952 | 28.79652176 | 31.56%
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

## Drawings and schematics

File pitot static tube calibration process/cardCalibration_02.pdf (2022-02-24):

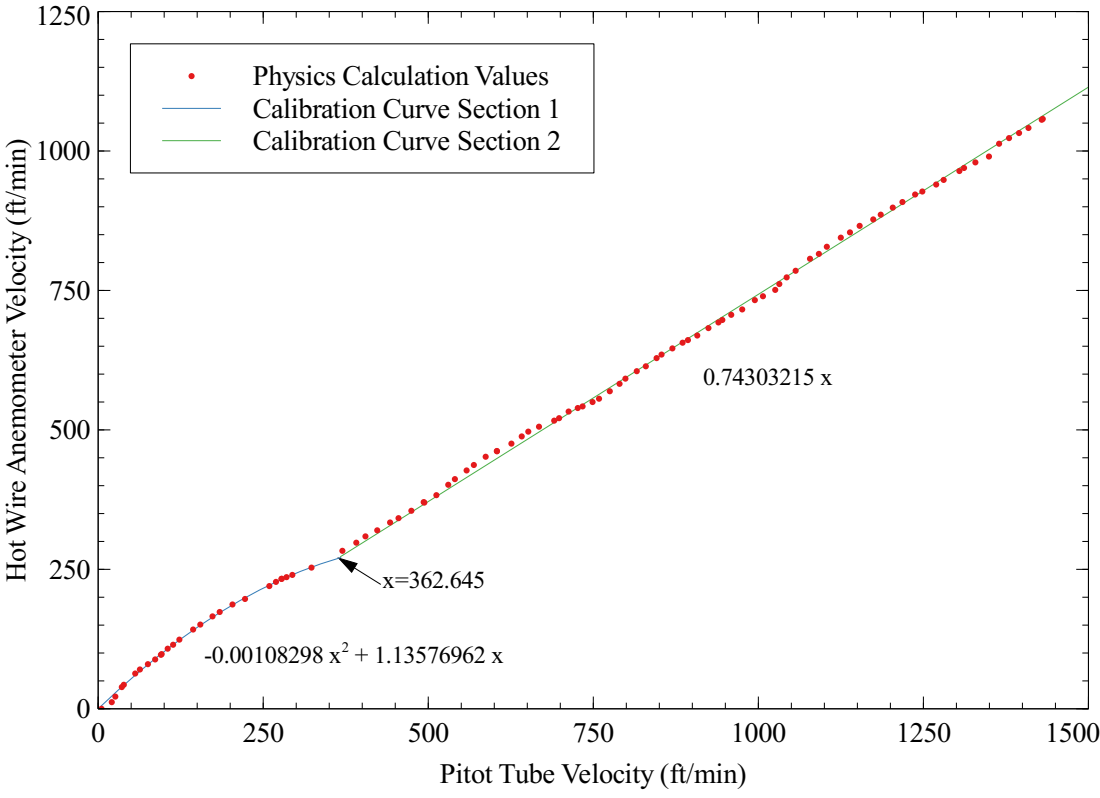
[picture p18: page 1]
C urv

Hot Wire Anemometer Velocity (ft/min)

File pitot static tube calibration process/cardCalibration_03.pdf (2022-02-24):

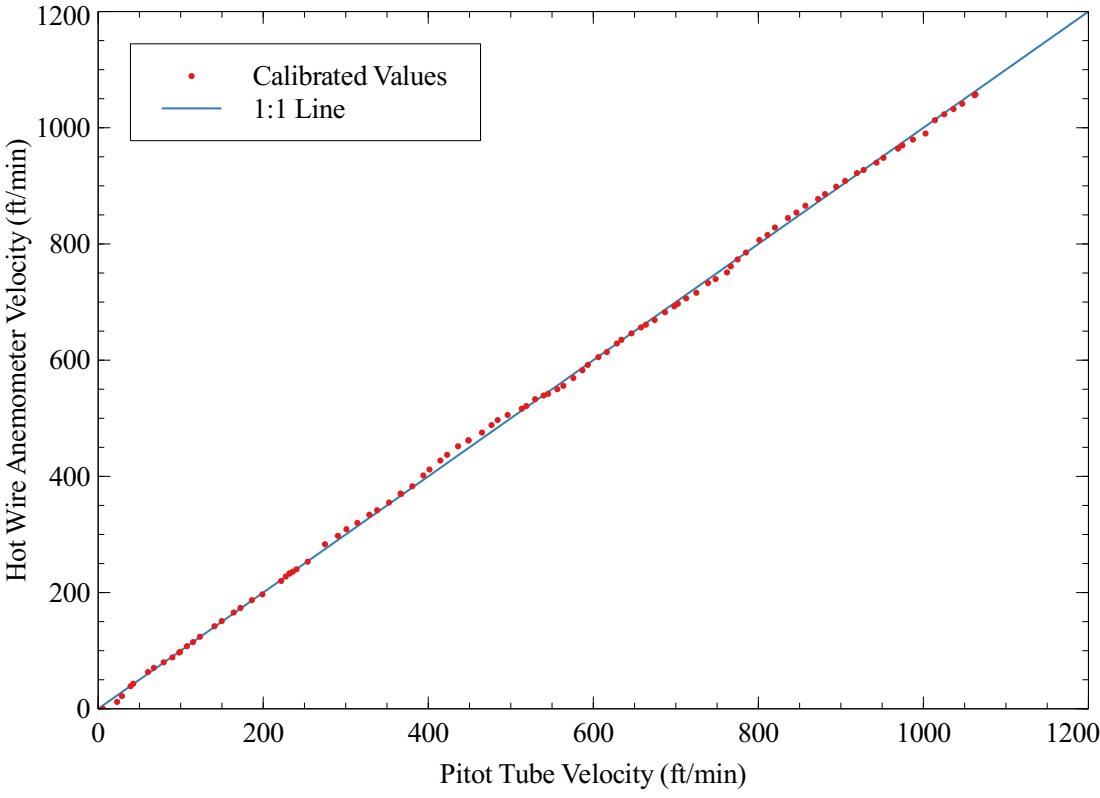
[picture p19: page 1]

Hot Wire Anemometer Velocity (ft/min)

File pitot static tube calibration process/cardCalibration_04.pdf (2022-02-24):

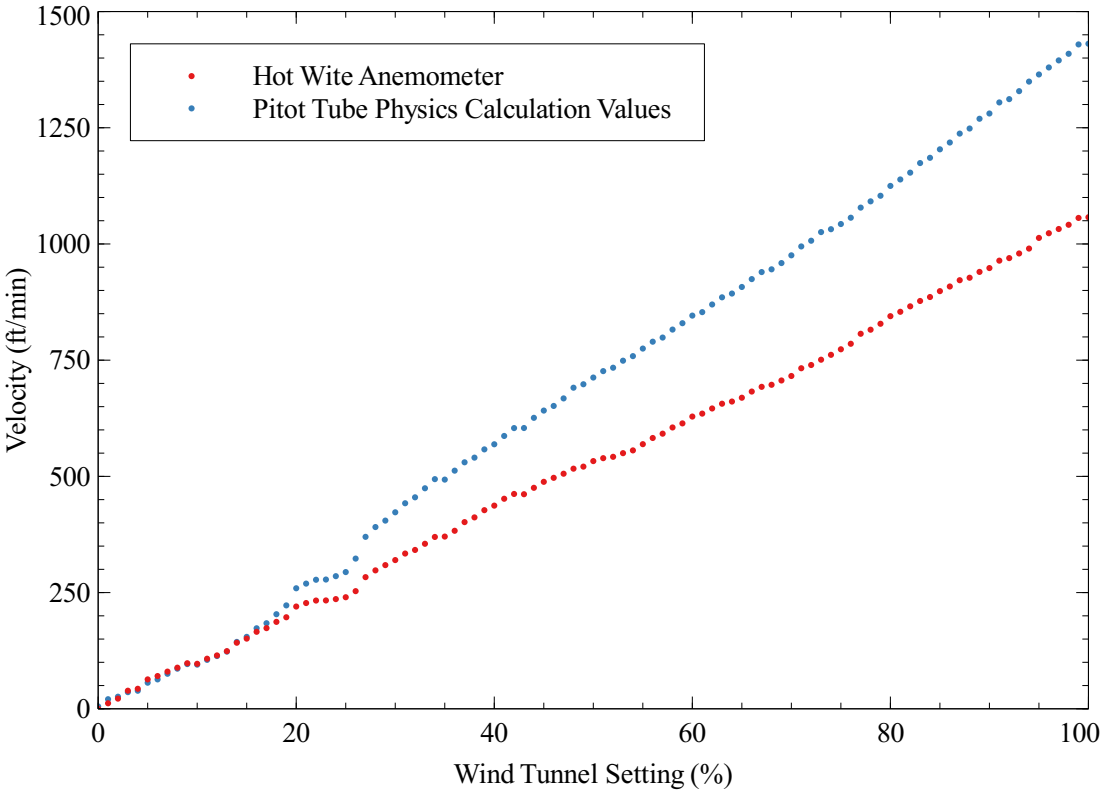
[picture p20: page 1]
Velo

Hot Wite Anemometer
Pitot Tube Physics Calculation Values

city (ft/min)

Wind Tunnel Setting (%)

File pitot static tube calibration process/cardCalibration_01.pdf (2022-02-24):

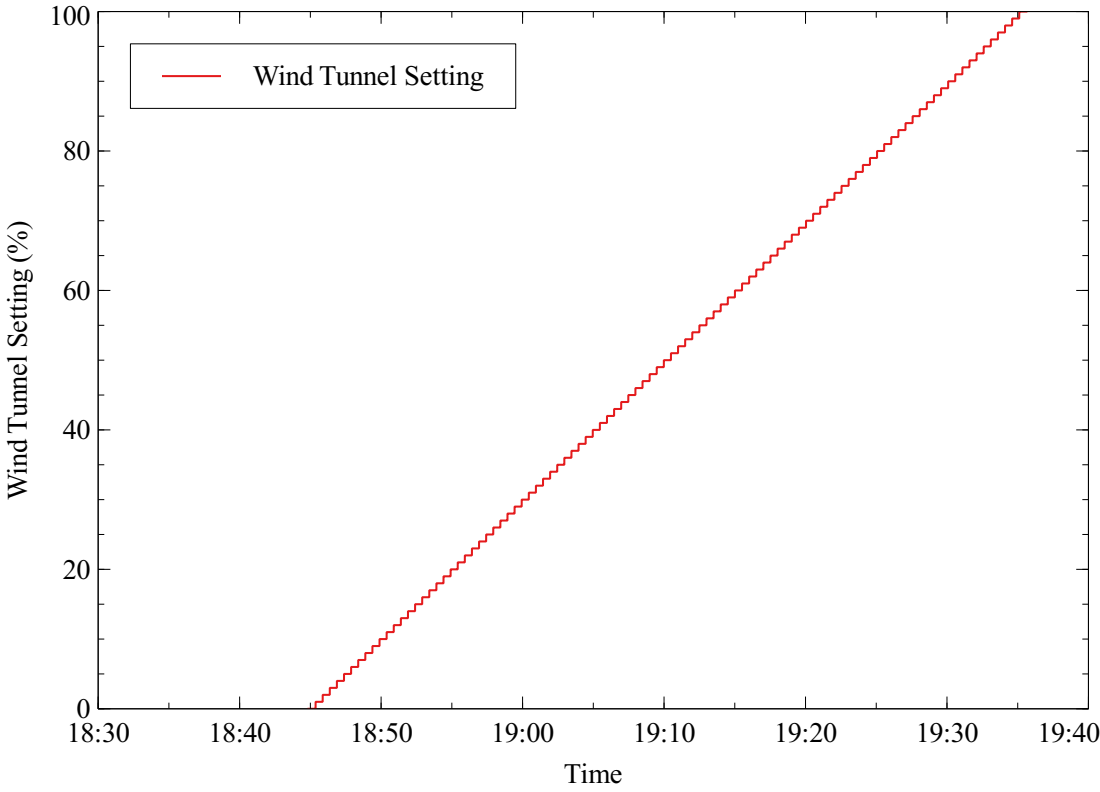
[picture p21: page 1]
Win; unn; ettin; Time

Wind Tunnel Setting

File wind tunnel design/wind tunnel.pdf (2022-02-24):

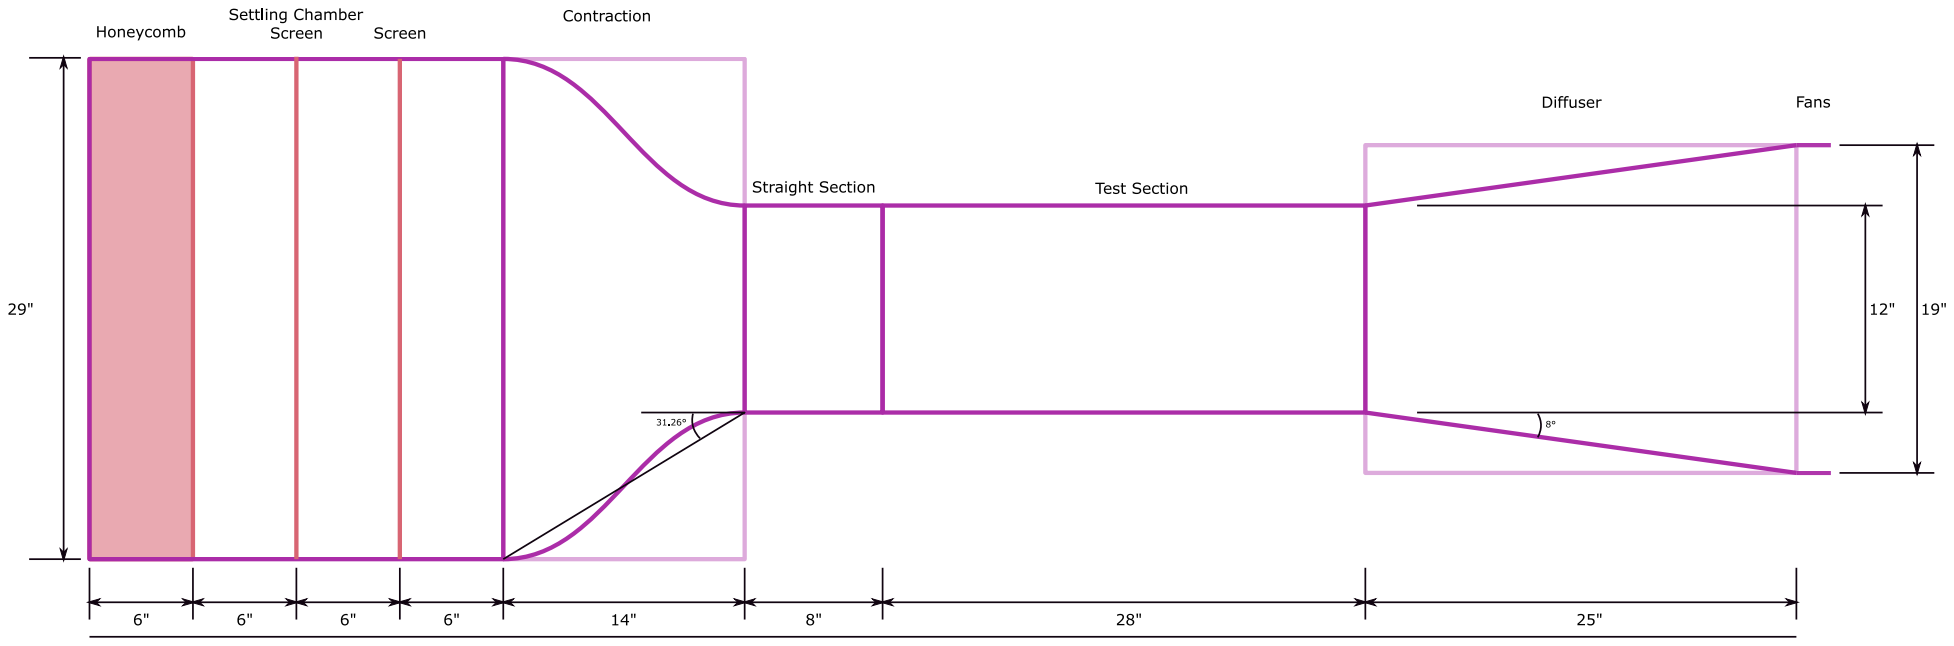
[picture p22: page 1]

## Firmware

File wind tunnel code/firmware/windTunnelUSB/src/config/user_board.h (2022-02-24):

/**
 * \file
 *
 * \brief User board definition template
 *
 */

 /* This file is intended to contain definitions and configuration details for
 * features and devices that are available on the board, e.g., frequency and
 * startup time for an external crystal, external memory devices, LED and USART
 * pins.
 */

#ifndef USER_BOARD_H
#define USER_BOARD_H

#include <compiler.h>
#include <conf_board.h>

//#define LED0                        LED0_GPIO
//#define LED1                        LED1_GPIO
//#define LED2                        LED2_GPIO
//#define LED3                        LED3_GPIO
//! Number of LEDs.
//#define LED_COUNT                   4
/*
#define FAN_0_PWM                   IOPORT_CREATE_PIN(PORTC, 0)
#define FAN_1_PWM                   IOPORT_CREATE_PIN(PORTC, 1)
#define FAN_2_PWM                   IOPORT_CREATE_PIN(PORTC, 2)
#define FAN_3_PWM                   IOPORT_CREATE_PIN(PORTC, 3)

#define SPI_PORT					SPIC
#define SPI_INT_VECTOR				SPIC_INT_vect
#define SPI_SS_PIN					IOPORT_CREATE_PIN(PORTC, 4)
#define SPI_MOSI_PIN				IOPORT_CREATE_PIN(PORTC, 5)
#define SPI_MISO_PIN				IOPORT_CREATE_PIN(PORTC, 6)
#define SPI_SCK_PIN					IOPORT_CREATE_PIN(PORTC, 7)


#define LED0_GPIO					IOPORT_CREATE_PIN(PORTB, 0)
#define LED1_GPIO                   IOPORT_CREATE_PIN(PORTB, 1)
#define LED2_GPIO                   IOPORT_CREATE_PIN(PORTB, 2)
#define LED3_GPIO                   IOPORT_CREATE_PIN(PORTB, 3)
*/

#define VARIABLE_RESISTOR		IOPORT_CREATE_PIN(PORTA,0)

#define FAN_PWM_A				IOPORT_CREATE_PIN(PORTC,0)
#define FAN_PWM_B				IOPORT_CREATE_PIN(PORTC,1)

#define UART_RX					IOPORT_CREATE_PIN(PORTD,2)
#define UART_TX					IOPORT_CREATE_PIN(PORTD,3)

#define LCD_RX					IOPORT_CREATE_PIN(PORTF,2)
#define LCD_TX					IOPORT_CREATE_PIN(PORTF,3)


#endif // USER_BOARD_H

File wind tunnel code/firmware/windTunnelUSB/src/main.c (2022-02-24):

/**
 * \file
 *
 * \brief CDC Application Main functions
 */

#include "asf.h"
#include "conf_usb.h"

#include "string.h"
#include "stdint.h"
#include "stdarg.h"

#include "usb_cdc_interface.h"
#include "pwm16.h"

#include <stdio.h>

struct pwm_config pwm_cfg_A;
struct pwm_config pwm_cfg_B;

// USART Serial is a debug interface connection
#define USART_SERIAL                     &USARTD0
#define USART_SERIAL_BAUDRATE            57600
#define USART_SERIAL_CHAR_LENGTH         USART_CHSIZE_8BIT_gc
#define USART_SERIAL_PARITY              USART_PMODE_DISABLED_gc
#define USART_SERIAL_STOP_BIT            false

// LCD serial connects to the character display
#define LCD_SERIAL                     &USARTF0
#define LCD_SERIAL_BAUDRATE            19200
#define LCD_SERIAL_CHAR_LENGTH         USART_CHSIZE_8BIT_gc
#define LCD_SERIAL_PARITY              USART_PMODE_DISABLED_gc
#define LCD_SERIAL_STOP_BIT            false

// ADC is the pot input used to set the fan pwm
#define MY_ADC    ADCA
#define MY_ADC_CH ADC_CH0

static volatile bool main_b_cdc_enable = false;
static volatile uint8_t main_port_open;


double pwm1 = 0;
double pwm2 = 0;
double percent = 0;
double percentCompensated = 0;

// Initialize the adc
static void adc_init(void)
{
	struct adc_config adc_conf;
	struct adc_channel_config adcch_conf;
	adc_read_configuration(&MY_ADC, &adc_conf);
	adcch_read_configuration(&MY_ADC, MY_ADC_CH, &adcch_conf);
	adc_set_conversion_parameters(&adc_conf, ADC_SIGN_OFF, ADC_RES_12, ADC_REF_VCC );
	adc_set_conversion_trigger(&adc_conf, ADC_TRIG_MANUAL, 1, 0);
	adc_set_clock_rate(&adc_conf, 200000UL);
	adcch_set_input(&adcch_conf, ADCCH_POS_PIN0, ADCCH_NEG_NONE, 1);
	adc_write_configuration(&MY_ADC, &adc_conf);
	adcch_write_configuration(&MY_ADC, MY_ADC_CH, &adcch_conf);
}

// write a string to the LCD
void lcd_puts (const char *send) {
	// Cycle through each character individually
	while (*send) {
		usart_putchar(LCD_SERIAL, *send++);
	}
}

// write a numeric value to the LCD
void lcd_print_value (uint16_t value) {
	char buffer[9];
	itoa((long)value, buffer, 10);
	lcd_puts(buffer);
}

// write a string to the debug uart
void uart_puts (const char *send) {
	// Cycle through each character individually
	while (*send) {
		usart_putchar(USART_SERIAL, *send++);
	}
}

// write a numeric value to the debug uart
void uart_print_value (uint16_t value) {
	char buffer[9];
	itoa((long)value, buffer, 10);
	uart_puts(buffer);
}

//-----------------------------------------------------------------------------

typedef struct {
	uint32_t	currentvalue;
	uint32_t	maxvalue;
} counter_overflow_t;

counter_overflow_t pwm_refresh = {0, 10}; //update every 10ms
counter_overflow_t tc_refresh  = {0, 1000}; //update every 2s

//-----------------------------------------------------------------------------

uint8_t verbose;
uint8_t tc_display_enable;


//-----------------------------------------------------------------------------

void process_command()
{

	char command_string[4];
	switch (command_in[0]) {
		
		case 'h': // Output help
		udi_cdc_puts("Help:");
		udi_cdc_puts("\r\n");
		udi_cdc_puts("'d' : disable pwms");
		udi_cdc_puts("\r\n");
		udi_cdc_puts("'e' : enable pwms");
		udi_cdc_puts("\r\n");
		udi_cdc_puts("'v' : toggle verbose output");
		udi_cdc_puts("\r\n");
		udi_cdc_puts("'s=00' : pwm value in hex");
		udi_cdc_puts("\r\n");
		break;
		
		case 'd': // disable pwms
			//pwm_refresh.enabled = 0;
			percent = 0;
			percentCompensated = 0;
			pwm1 = 0;
			pwm2 = 0;
			pwm_set_duty_cycle_percent(&pwm_cfg_A, pwm1);
			pwm_set_duty_cycle_percent(&pwm_cfg_B, pwm2);
			if (verbose) {
				udi_cdc_puts("PWM outputs disabled");
				udi_cdc_puts("\r\n");
			}
		break;
		
		case 'e': // enable pwms
			//pwm_refresh.enabled = 1;
			udi_cdc_puts("PWM outputs enabled");
			udi_cdc_puts("\r\n");
		break;
		
		case 'v': // toggle  verbose output
			if (verbose) {
				verbose=0;
				udi_cdc_puts("Verbose output disabled");
				udi_cdc_puts("\r\n");
			} else {
				verbose=1;
				udi_cdc_puts("Verbose output enabled");
				udi_cdc_puts("\r\n");
			}
			//udi_cdc_puts("\n\r");
		break;
		
		case 's': //simulate spi input
			if (command_in[1] == '=') {
				//input must be in the format s=xx
				// first is the address, second two are the pwm values, third two are the duration

				//http://www.dfstermole.net/OAC/hstrings.html
				strncpy(command_string, &command_in[2], 4);
				command_string[3]='\0';
				percent = strtol(command_string, NULL, 10);
				//data_buffer[bytes_received] = atoi(channel_address);
	
				// Set valid range for percent
				if (percent < 0) {
					percent = 0;
				}
				if (percent > 100) {
					percent = 100;
				}


				double percentSquared = percent*percent;
				double percentCubed = percentSquared*percent;
								
				if (percent < 20) {
					//percentCompensated = 0.003001*percentCubed - 0.042495*percentSquared + 0.898157*percent - 0.053577;
					percentCompensated = 0.002351*percentCubed - 0.028552*percentSquared + 0.830766*percent - 0.039634;
				} else {
					//percentCompensated = 0.000082*percentCubed - 0.010512*percentSquared + 1.164923*percent + 5.749069;
					percentCompensated = 0.000083*percentCubed - 0.010387*percentSquared + 1.132475*percent + 7.080597;
				}
	
				//percentCompensated = percent;			
				
				/*
				// pwm1 should never be below 0.  pwm2 will sometimes goe negative (based on curve fit) but really should be limited to 0
				if (pwm1 < 0) {
					pwm1 = 0;
				}
				if (pwm2 < 0) {
					pwm2 = 0;
				}
				
				// This should never happen but put in for safety check
				if (pwm1 > 100) {
					pwm1 = 100;
				}
				if (pwm2 > 100) {
					pwm2 = 100;
				}
*/
				
				// calculate pwm percentages
				// scale the pwm outputs so one turns off before the other (to get more low end resolution)
				pwm1 = (percentCompensated*0.90) + 10;
				pwm2 = (percentCompensated-20) * 1.25;
				
				if (pwm1 < 0.0) {
					pwm1 = 0.0;
				} else if (pwm1 > 100.0) {
					pwm1 = 100.0;
				}
				
				if (pwm2 < 0.0) {
					pwm2 = 0.0;
				} else if (pwm2 > 100.0) {
					pwm2 = 100.0;
				}
				
				
				pwm_set_duty_cycle_percent(&pwm_cfg_A, (uint8_t)pwm1);
				pwm_set_duty_cycle_percent(&pwm_cfg_B, (uint8_t)pwm2);
		
				if (verbose) {
					udi_cdc_puts("command in=");
					udi_cdc_puts(command_in);
					udi_cdc_puts(", command string=");
					udi_cdc_puts(command_string);
					udi_cdc_puts(", percent=");
					print_value32(percent);
					udi_cdc_puts(", pwm1=");
					print_value32(pwm1);
					udi_cdc_puts(", pwm2=");
					print_value32(pwm2);
					udi_cdc_puts("\r\n");
				} 
			}				
		break;
		
		case 'g': // display settings
			if (verbose) {
				udi_cdc_puts("percent=");
				print_value32(percent);
				udi_cdc_puts(", pwm1=");
				print_value32(pwm1);
				udi_cdc_puts(", pwm2=");
				print_value32(pwm2);
				udi_cdc_puts("\r\n");
			} else {
				print_value32(percent);
				udi_cdc_puts(",");
				print_value32(pwm1);
				udi_cdc_puts(",");
				print_value32(pwm2);
				udi_cdc_puts("\r\n");
			}
		break;
	
		
		default:
			udi_cdc_puts("NOT RECOGNISED.  Enter h for list of commands");
			udi_cdc_puts("\r\n");
		break;
	}
}



/*! \brief Main function. Execution starts here.
 */
int main(void)
{
	irq_initialize_vectors();
	cpu_irq_enable();

	// Initialize the sleep manager
	sleepmgr_init();

	sysclk_init();
	
	// configure debug uart
	static usart_rs232_options_t USART_SERIAL_OPTIONS = {
		.baudrate = USART_SERIAL_BAUDRATE,
		.charlength = USART_SERIAL_CHAR_LENGTH,
		.paritytype = USART_SERIAL_PARITY,
		.stopbits = USART_SERIAL_STOP_BIT
	};
	sysclk_enable_module(SYSCLK_PORT_D, PR_USART0_bm);
	usart_init_rs232(USART_SERIAL, &USART_SERIAL_OPTIONS);
	
	// config lcd uart
	static usart_rs232_options_t LCD_SERIAL_OPTIONS = {
		.baudrate = LCD_SERIAL_BAUDRATE,
		.charlength = LCD_SERIAL_CHAR_LENGTH,
		.paritytype = LCD_SERIAL_PARITY,
		.stopbits = LCD_SERIAL_STOP_BIT
	};
	sysclk_enable_module(SYSCLK_PORT_F, PR_USART0_bm);
	usart_init_rs232(LCD_SERIAL, &LCD_SERIAL_OPTIONS);
	
	board_init();
	
	pmic_init();

	// dont need these two ui things
	//	ui_init();
	//	ui_powerdown();

	// initialize the pwms at 24kHx
	pwm_init(&pwm_cfg_A, PWM_TCC0, PWM_CH_A, 24000);
	pwm_init(&pwm_cfg_B, PWM_TCC0, PWM_CH_B, 24000);

	// initialize fans at 0% then wait for 2s before starting
	pwm_start(&pwm_cfg_A, 0);
	pwm_start(&pwm_cfg_B, 0);

	// Display boot screen on lcd

	// clear screen
	usart_putchar(LCD_SERIAL, 0xFE);
	usart_putchar(LCD_SERIAL, 0x58);

	// Go home
	usart_putchar(LCD_SERIAL, 0xFE);
	usart_putchar(LCD_SERIAL, 0x48);

	lcd_puts("     Wind Tunnel");
	// Set cursor position
	usart_putchar(LCD_SERIAL, 0xFE);
	usart_putchar(LCD_SERIAL, 0x47);
	usart_putchar(LCD_SERIAL, 0x01); // col
	usart_putchar(LCD_SERIAL, 0x02); // row
	lcd_puts("    ramping fans");

	// delay for 2s while fans ramp up to 50%
	delay_ms(2000);

	// initialize the adc
	//adc_init();
	//adc_enable(&MY_ADC);

	// clear lcd before starting loop

	// clear screen
	//usart_putchar(LCD_SERIAL, 0xFE);
	//usart_putchar(LCD_SERIAL, 0x58);

	// Initialize Horizontal Bar
	//usart_putchar(LCD_SERIAL, 0xFE);
	//usart_putchar(LCD_SERIAL, 0x68);

	// Start USB stack to authorize VBus monitoring
	udc_start();

	// The main loop manages only the power mode
	// because the USB management is done by interrupt
	while (true) {
		sleepmgr_enter_sleep();
		
		if (command_ready == 1) {
			copy_command();
			process_command();
			command_ready = 0;
		}
	}
}

void main_suspend_action(void)
{
	//ui_powerdown();
}

void main_resume_action(void)
{
	//ui_wakeup();
}

void main_sof_action(void)
{
	if (!main_b_cdc_enable)
		return;
	//ui_process(udd_get_frame_number());
}

bool main_cdc_enable(uint8_t port)
{
	main_b_cdc_enable = true;
	main_port_open = 0;
	// Open communication
	//uart_open(port);
	return true;
}

void main_cdc_disable(uint8_t port)
{
	main_b_cdc_enable = false;
	// Close communication
	//uart_close(port);
}

void main_cdc_set_dtr(uint8_t port, bool b_enable)
{
	if (b_enable) {
		// Host terminal has open COM
		main_port_open |= 1 << port;
		//ui_com_open(port);
	}else{
		// Host terminal has close COM
		main_port_open &= ~(1 << port);
		//ui_com_close(port);
	}
}

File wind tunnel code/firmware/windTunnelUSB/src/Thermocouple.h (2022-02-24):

/**
@file Thermocouple.h

@brief Driver for Multiplexed AD849x Thermocouple Reader Board
@details Type K thermocouples read using AD849x.  8 channel multiplexed.

Usage:

@code
#include "LK202_25.h"
#include "UART_polled.h"
#include "adc_atmega32u4.h"
#include "Thermocouple.h"

int main (void) {
	uint8_t string_size = 21; //including null terminator
	char string_buffer[string_size];
	double temperature_values[8];

	InitUART();
	_delay_ms(500);
	LCD_init();
	thermocouple_init();

	while (1) {
		LCD_home();
		
		// Loop through each thermocouple on the multiplexer and read its value
		for (uint8_t scount=0; scount<8; scount++){
			temperature_values[scount] = thermocouple_read(scount, 100);
		}
		
		snprintf(string_buffer,string_size,"%4.1f %4.1f %4.1f %4.1f",temperature_values[0],temperature_values[1],temperature_values[2],temperature_values[3]);
		LCD_printstring(string_buffer);
		
		LCD_goto(1,2);
		snprintf(string_buffer,string_size,"%4.1f %4.1f %4.1f %4.1f",temperature_values[4],temperature_values[5],temperature_values[6],temperature_values[7]);
		LCD_printstring(string_buffer);

		_delay_ms(100);
	}
	return 0;
}
@endcode

@author Phil Spindler
@date 8/26/2013
*/


#ifndef THERMOCOUPLE_H_
#define THERMOCOUPLE_H_

#include "inttypes.h"


//#define TC_SELECT_PORT	PORTA /**< Port that the multiplexer select pins are connected to */
//#define TC_SELECT_R		PORTA_DIR //DDRA /**< Port register that the multiplexer select pins are connected to */
//#define TC_SELECT_0	 	PINA7 /**< Pin that multiplexer select 0 is connected to */
//#define TC_SELECT_1		PINA6 /**< Pin that multiplexer select 1 is connected to */
//#define TC_SELECT_2		PINA5 /**< Pin that multiplexer select 2 is connected to */
//#define TC_REF		1 /**< ADC pin number that the thermocouple offset voltage is connected to (pin A1 = ADC channel 1) */
//#define TC_IN		2 /**< ADC pin number that the AD849x thermocouple output is connected to (pin A2 = ADC channel 2) */



/* Cable Pinout
  TC   -    uC
  3.3   1-1  3.3
  GND   2-2  GND
  Sel0  3-3  PA7
  Sel1  4-4  PA6
  Sel2  5-5  PA5
  Out   6-8  PA2
  Ref   7-9  PA1
  NC    8-NC
  */
#define TC_SELECT_0	 	IOPORT_CREATE_PIN(PORTA, 7) /**< Pin that multiplexer select 0 is connected to */
#define TC_SELECT_1		IOPORT_CREATE_PIN(PORTA, 6) /**< Pin that multiplexer select 1 is connected to */
#define TC_SELECT_2		IOPORT_CREATE_PIN(PORTA, 5) /**< Pin that multiplexer select 2 is connected to */

#define TC_ADC		ADCA
#define TC_REF		ADC_CH1 /**< ADC pin number that the thermocouple offset voltage is connected to (pin A1 = ADC channel 1) */
#define TC_IN		ADC_CH2 /**< ADC pin number that the AD849x thermocouple output is connected to (pin A2 = ADC channel 2) */



/**
* Initialize ADC and the pins used for multiplexer selection
*
*
*/
void thermocouple_init(void);
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
